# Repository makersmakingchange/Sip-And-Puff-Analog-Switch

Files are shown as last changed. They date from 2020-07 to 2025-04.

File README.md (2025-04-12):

# Sip and Puff Switch

The Sip and Puff Switch is an assistive technology that enables a user to control a device by using their mouth to "sip"(inhale) or "puff"(exhale) on a straw, tube or ‘wand’. It is primarily used by people with limited or no limb movement. The Sip and Puff Switch can be connected directly to an assistive device with a 3.5 mm jack or to a computer or smartphone using a suitable switch interface.

The Sip and Puff Switch has two 3.5 mm mono outputs so it can control two devices. The sip threshold and puff threshold are adjustable. The switch is powered by two CR2032 lithium coin cell batteries.

## More info at

- [Makers Making Change Project Page](https://www.makersmakingchange.com/project/sip-and-puff-switch/)

## Getting Started

### 1. Order the Off-The-Shelf Components
The [Bill of Materials](/Documentation/SPA_BOM_v1.0.xlsx) lists all of the parts and components required to build the Sip and Puff switch.

### 2. Order the Custom Printed Circuit Board (PCB)
The Sip and Puff Switch uses a custom PCB to mount all of the electronic components. Refer to [MMC_PCB_Fabrication_Manual](/Documentation/MMC_PCB_Fabrication_Manual.pdf) for information on how to order a custom PCB. For convenience, the final generated Gerber files for several PCB manufacturers are listed below. If you want to use a different manufacturer, instructions for converting the original [Eagle Files](/Design_Files/PCB/Eagle_Files) are also included in the MMC PCB Fabrication Manual.

| PCB Manufacturer                	| Website                                 	| Gerber Files                                                                                                        	|
|---------------------------------	|-----------------------------------------	|-------------------------------------------------------------------------------------------------------------	|
| JLCPCB                          	| https://jlcpcb.com/                     	|  [JLCPCB_Sip_And_Puff_Analog_Switch.zip](/Build_Files/PCB/JLCPCB_Sip_And_Puff_Analog_Switch.zip)             	|
| OSH Park                        	| https://oshpark.com/                    	| [OSHPark_Sip_And_Puff_Analog_Switch.zip](/Build_Files/PCB/OSHPark_Sip_And_Puff_Analog_Switch.zip)           	|
| Seeed Fusion PCB                	| https://www.seeedstudio.com/fusion.html 	| [Seeed_Fusion_Sip_And_Puff_Analog_Switch.zip](/Build_Files/PCB/Seeed_Fusion_Sip_And_Puff_Analog_Switch.zip) 	|

### 3. Print the 3D Printable components

Print the components for the enclosure and the mouthpiece mount: [3D Printing Files](/Build_Files/3D_Printing/). Total print time for the enclosure components is approximately 4.5 hours and for the mouthpiece mount components is approximately 2.5 hours.  

### 4. Assemble the Switch and Mouthpiece Mount

Reference the assembly instructions for the [Sip and Puff Switch](/Documentation/SPA_Assembly_v1.0.pdf) and the assembly instructions for the [Mouthpiece Stand](/Documentation/SPA_MPStand_Assembly_v1.0.pdf) for the tools and steps required to build each portion.

## Files

### Documentation
| Document                        	| Version 	| Link                                                                         	|
|---------------------------------	|---------	|------------------------------------------------------------------------------	|
| Design Specification            	| WIP     	|                                                                              	|
| Design Rationale                	| WIP     	|                                                                              	|
| Bill of Materials               	| 1.0     	| [SPA_BOM](/Documentation/SPA_BOM_v1.0.xlsx)                                  	|
| Assembly Guide                  	| 1.0     	| [SPA_Assembly](/Documentation/SPA_Assembly_v1.0.pdf)                         	|
| Mouthpiece Mount Assembly Guide 	| 1.0     	| [SPA_MPStand_Assembly](/Documentation/SPA_MPStand_Assembly_v1.0.pdf)         	|
| Maker Checklist                 	| 1.0     	| [SPA_Checklist](/Documentation/SPA_Checklist_v1.0.pdf)                       	|
| Quick Guide                     	| 1.0     	| [SPA_Checklist](/Documentation/SPA_Quick_Guide_v1.0.pdf)                      |
| User Guide                      	| 1.0     	| [SPA_Checklist](/Documentation/SPA_User_Guide_v1.0.pdf)                       |
| Changelog                       	| 1.0     	| [SPA_Changelog](/Documentation/SPA_Changelog_v1.0.pdf)                       	|
| PCB Fabrication Manual          	| 0.1     	| [MMC_PCB_Fabrication_Manual](/Documentation/MMC_PCB_Fabrication_Manual.pdf)  	|

### Design Files
 - [Enclosure CAD Files](/Design_Files/CAD/Enclosure)
 - [Mouthpiece Mount CAD Files](/Design_Files/CAD/Mouthpiece_Mount)
 - [PCB Files](/Design_Files/PCB/Eagle_Files)

### Build Files
 - [3D Printing Files](/Build_Files/3D_Printing)
 - [PCB Files](/Build_Files/PCB/Gerber_Files)

## License
Everything needed or used to design, make, test, or prepare the Analog Sip and Puff Switch is licensed under the CERN 2.0 Persmissive license <https://ohwr.org/project/cernohl/wikis/Documents/CERN-OHL-version-2> (CERN-OHL-P) .

Accompanying material such as instruction manuals, videos, and other copyrightable works that are useful but not necessary to design, make, test, or prepare the Analog Sip and Puff Switch are publshed under a Creative Commons Attribution-ShareAlike 4.0 license <https://creativecommons.org/licenses/by-sa/4.0/> (CC BY-SA 4.0)

<!-- ABOUT MMC START -->
## About Makers Making Change
[Makers Making Change Logo](https://www.makersmakingchange.com/)

Makers Making Change is a program of [Neil Squire](https://www.neilsquire.ca/), a Canadian non-profit that uses technology, knowledge, and passion to empower people with disabilities.

Makers Making Change leverages the capacity of community based Makers, Disability Professionals and Volunteers to develop and deliver affordable Open Source Assistive Technologies.

 - Website: [www.MakersMakingChange.com](https://www.makersmakingchange.com/)
 - GitHub: [makersmakingchange](https://github.com/makersmakingchange)
 - Bluesky: [@makersmakingchange.bsky.social](https://bsky.app/profile/makersmakingchange.bsky.social)
 - Instagram: [@makersmakingchange](https://www.instagram.com/makersmakingchange)
 - Facebook: [makersmakechange](https://www.facebook.com/makersmakechange)
 - LinkedIn: [Neil Squire Society](https://www.linkedin.com/company/neil-squire-society/)
 - Thingiverse: [makersmakingchange](https://www.thingiverse.com/makersmakingchange/about)
 - Printables: [MakersMakingChange](https://www.printables.com/@MakersMakingChange)

### Contact Us
For technical questions, to get involved, or to share your experience we encourage you to [visit our website](https://www.makersmakingchange.com/) or [contact us](https://www.makersmakingchange.com/s/contact).
<!-- ABOUT MMC END -->

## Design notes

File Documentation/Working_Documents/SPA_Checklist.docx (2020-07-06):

To-do

- Acquire off-the-shelf components
- Print 3D printable components
- Assemble the switch
- Test the switch
- Clean and disinfect the switch
- Package the switch in a sealed bag
- Print the Quick Guide

Items to Deliver to User

- Assembled, Tested, and cleaned Sip and Puff Switch
- Quick Guide

© 2020 by Neil Squire. “Sip and Puff Switch Maker Checklist” is licensed under the CC BY SA 4.0 License: http://creativecommons.org/licenses/by-sa/4.0 PAGE 1 OF 3 Design files available at https://www.makersmakingchange.com/project/sip-and-puff-switch/

V1.0 | JUNE 2020 Sip and Puff Switch MAKER CHECKLIST

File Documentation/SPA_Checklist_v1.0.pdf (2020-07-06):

V1.0 | JUNE 2020

# Sip and Puff Switch

MAKER CHECKLIST

© 2020 by Neil Squire. (https://neilsquire.ca/) “Sip and Puff Switch Maker Checklist” is licensed under the CC BY SA 4.0 License: http://creativecommons.org/licenses/by-sa/4.0

Design files available at https://www.makersmakingchange.com/project/sip-and-puff-switch/ | PAGE 1 OF 1

To-do

ð Acquire off-the-shelf components ð Print 3D printable components ð Assemble the switch
ð Test the switch
ð Clean and disinfect the switch
ð Package the switch in a sealed bag ð Print the Quick Guide

Items to Deliver to User

ð Assembled, Tested, and cleaned Sip and Puff Switch
ð Quick Guide

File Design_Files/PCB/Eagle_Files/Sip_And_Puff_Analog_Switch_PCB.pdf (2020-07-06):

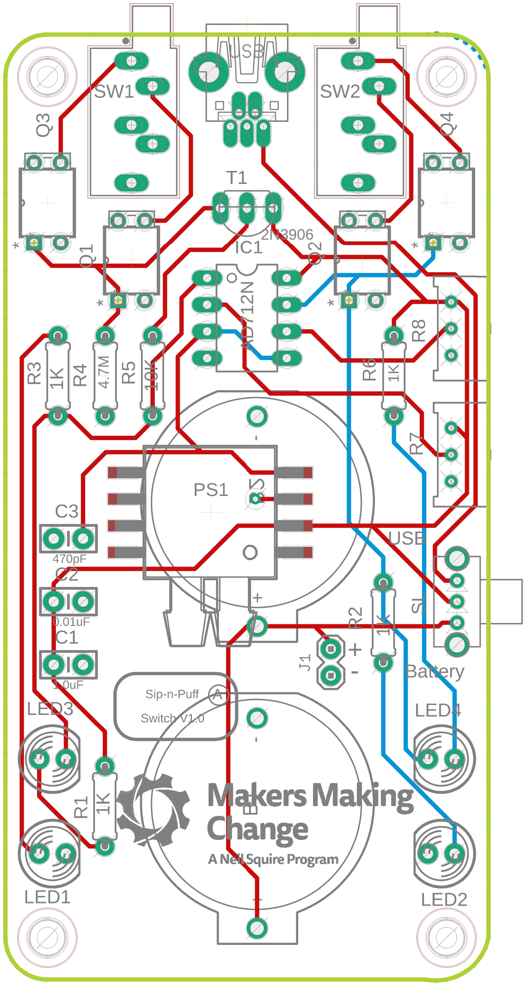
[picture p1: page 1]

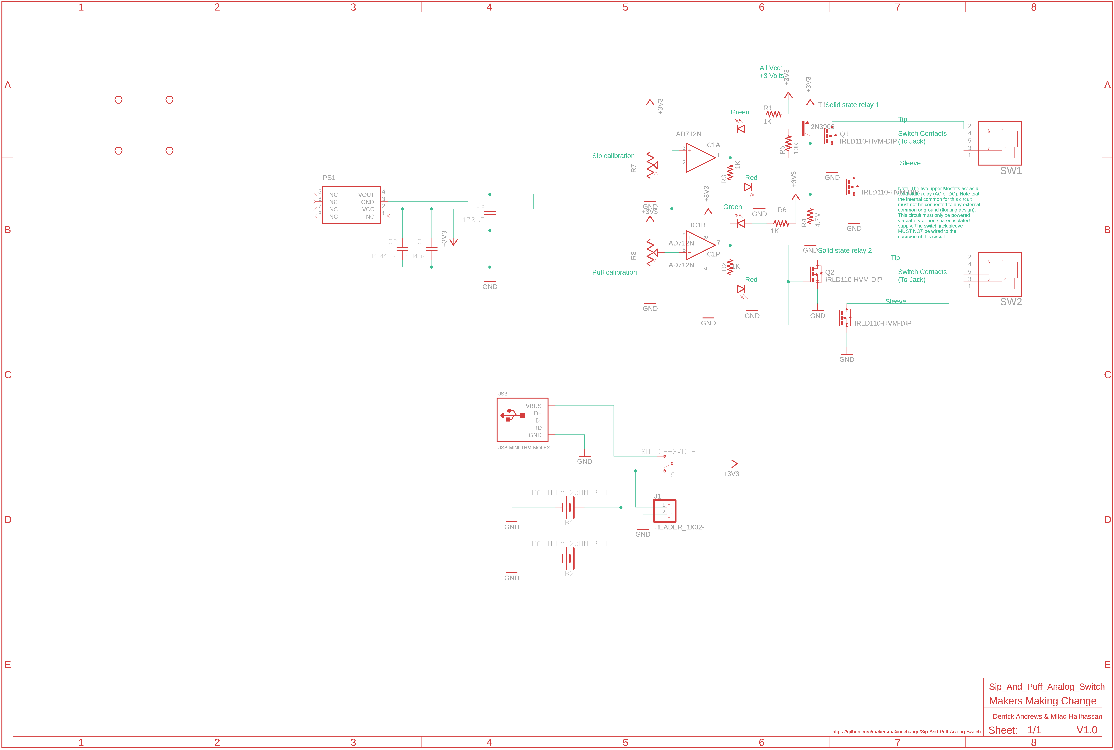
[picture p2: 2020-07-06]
Design_Files/PCB/Eagle_Files/Sip_And_Puff_Analog_Switch_sch.png

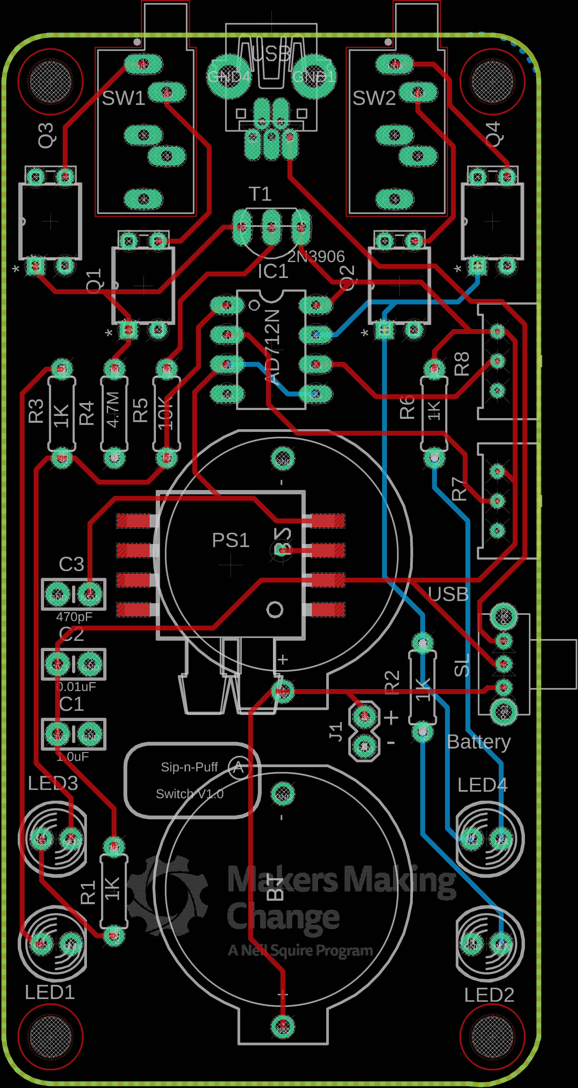
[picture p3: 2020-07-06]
Design_Files/PCB/Eagle_Files/Sip_And_Puff_Analog_Switch_brd.png

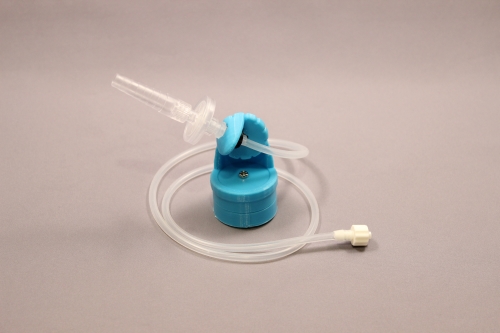
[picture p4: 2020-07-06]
Photos/SPA_Mouthpiece_Mount.JPG

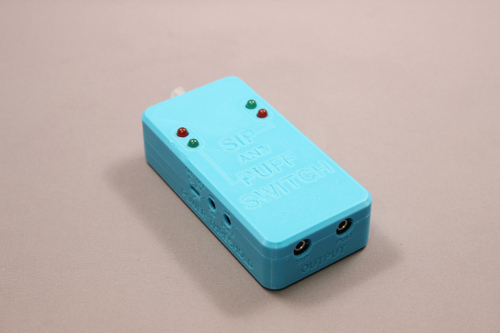
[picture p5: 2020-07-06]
Photos/SPA_Enclosure.JPG

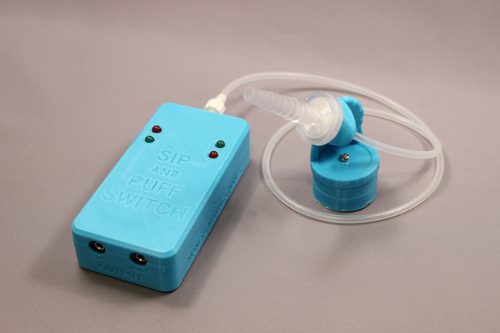
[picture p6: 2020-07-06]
Photos/Sip-And-Puff-Switch.JPG

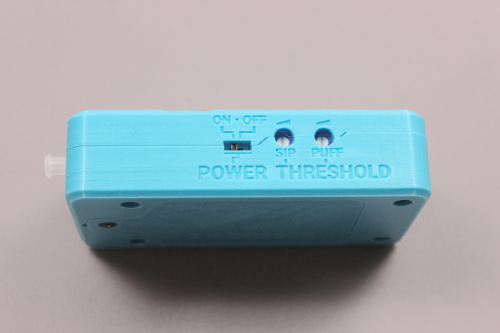
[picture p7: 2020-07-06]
Photos/SPA_Enclosure2.JPG

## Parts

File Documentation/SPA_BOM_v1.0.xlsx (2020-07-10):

ID | SubAssembly | Type | Qty | Component | Component name | Vendor | Manufacturer | MPN | Part Number | Pkg Qty | Pkg Cost (CAD) | Unit Cost | Pkg ReqD | MinCost | Extended Cost (CAD) | Sub-Assembly | Link
 | Switch |  |  |  | Sip and Puff Switch |  |  |  |  |  |  |  |  | $285.00 |  | $111.53
 | PCB Component |  |  |  |  |  |  |  |  |  |  |  |  |  |  | $48.26
 | PCB Component | COTS | 1 | PS1 | IC PRESSURE SENSOR 8-SOP 3V | Digikey Canada | NXP USA Inc. | MP3V5004GP-ND | MP3V5004GP-ND | 1 | $21.94 | 21.94 | 1 | $21.94 | $21.94 |  | https://www.digikey.ca/products/en?keywords=MP3V5004GP-ND
 | PCB Component | COTS | 2 | SW1,SW2 | CONN JACK STEREO 3.5MM R/A | Digikey Canada | CUI Devices | SJ1-3535NG | CP1-3535NG-ND | 1 | $1.70 | 1.7 | 2 | $3.40 | $3.40 |  | https://www.digikey.ca/product-detail/en/cui-devices/SJ1-3535NG/CP1-3535NG-ND/738699
 | PCB Component | COTS | 1 | IC1 | OP AMP 2Ch RR | Digikey Canada | Microchip inc. | MCP6002-I/P | MCP6002-I/P-ND | 1 | $2.16 | 2.16 | 1 | $2.16 | $2.16 |  | https://www.digikey.ca/product-detail/en/microchip-technology/MCP6002-I-P/MCP6002-I-P-ND/500875
 | PCB Component | COTS | 2 | LED2,LED4 | GREEN LED | Digikey Canada | Lite-On Inc. |  | 160-1852-ND | 1 | $0.50 | 0.5 | 2 | $1.00 | $1.00 |  | https://www.digikey.ca/products/en?keywords=LTL2R3KGD-EM
 | PCB Component | COTS | 1 | C3 | CAP CER 470PF 50V X7R RADIAL | Digikey Canada | KEMET | C315C471K5R5TA | 399-9740-ND | 1 | $0.50 | 0.5 | 1 | $0.50 | $0.50 |  | http://www.digikey.ca/product-detail/en/kemet/C315C471K5R5TA/399-9740-ND
 | PCB Component | COTS | 1 | C2 | CAP CER 10000PF 50V X7R RADIAL | Digikey Canada | KEMET | C315C103K5R5TA7303 | 399-9858-1-ND | 1 | $0.37 | 0.37 | 1 | $0.37 | $0.37 |  | https://www.digikey.ca/product-detail/en/kemet/C315C103K5R5TA7303/399-9858-1-ND
 | PCB Component | COTS | 1 | C1 | CAP CER 1UF 25V X7R RADIAL | Digikey Canada | KEMET | C315C105K3R5TA | 399-9714-ND | 1 | $1.13 | 1.13 | 1 | $1.13 | $1.13 |  | https://www.digikey.ca/product-detail/en/kemet/C315C105K3R5TA/399-9714-ND
 | PCB Component | COTS | 2 | LED1,LED3 | RED LED | Digikey Canada | Lite-On Inc. | LTL2R3KRD-EM | 160-1853-ND | 1 | $0.50 | 0.5 | 2 | $1.00 | $1.00 |  | https://www.digikey.ca/en/products/detail/lite-on-inc/LTL2R3KRD-EM/2675133
 | PCB Component | COTS | 1 | SL | SWITCH SLIDE SPDT 100MA 12V | Digikey Canada | C&K | OS102011MA1QN1 | CKN9559-ND | 1 | $0.73 | 0.73 | 1 | $0.73 | $0.73 |  | https://www.digikey.ca/product-detail/en/c-k/OS102011MA1QN1/CKN9559-ND/1981430
 | PCB Component | COTS | 4 | Q1-Q4 | MOSFET N-CH 100V 1A 4-DIP | Digikey Canada | Vishay Siliconix | IRLD110PBF | IRLD110PBF-ND | 1 | $1.32 | 1.32 | 4 | $5.28 | $5.28 |  | https://www.digikey.ca/product-detail/en/vishay-siliconix/IRLD110PBF/IRLD110PBF-ND/812489
 | PCB Component | COTS | 1 | Q5 | TRANSISTOR, PNP 2N3906 | Digikey Canada | ON Semiconductor | 2N3906 | 2N3906D26ZCT-ND | 1 | $0.34 | 0.34 | 1 | $0.34 | $0.34 |  | https://www.digikey.ca/product-detail/en/fairchild-on-semiconductor/2N3906TFR/2N3906D26ZCT-ND
 | PCB Component | COTS | 2 | B1 B2 | Battery holder | Digikey Canada | MPD (Memory Protection Devices) | BS-7 | BS-7-ND | 1 | $1.19 | 1.19 | 2 | $2.38 | $2.38 |  | https://www.digikey.ca/product-detail/en/mpd-memory-protection-devices/BS-7/BS-7-ND/389447
 | PCB Component | COTS | 1 | R4 | 4.7M RESISTOR | Digikey Canada | STACKPOLE | CF14JT4M70 | CF14JT4M70CT-ND | 1 | $0.16 | 0.16 | 1 | $0.16 | $0.16 |  | https://www.digikey.ca/en/products/detail/stackpole-electronics-inc/CF14JT4M70/1741430
 | PCB Component | COTS | 1 | R5 | 10K RESISTOR | Digikey Canada | STACKPOLE | CF14JT10K0CT | CF14JT10K0CT-ND | 1 | $0.16 | 0.16 | 1 | $0.16 | $0.16 |  | https://www.digikey.ca/products/en?keywords=CF14JT10K0CT-ND
 | PCB Component | COTS | 4 | R1,R2,R3,R6 | 1K RESISTOR | Digikey Canada | STACKPOLE | CF14JT1K00 | CF14JT1K00-ND | 1 | $0.16 | 0.16 | 4 | $0.64 | $0.64 |  | https://www.digikey.ca/en/products/detail/stackpole-electronics-inc/CF14JT1K00/1741314
 | PCB Component | COTS | 1 | J1 | CONN HEADER VERT 2POS 2.54MM | Digikey Canada | Sullins Connector Solutions | PREC002SAAN-RC | S1012EC-02-ND | 1 | $0.09 | 0.09 | 1 | $0.09 | $0.09 |  | https://www.digikey.ca/en/products/detail/sullins-connector-solutions/PREC002SAAN-RC/2774852
 | PCB Component | COTS | 2 | R7,R8 | 10K TRIMMER RESISTOR | Digikey Canada | Bourns Inc. | 3386C-103LF | 3386C-103LF-ND | 1 | $3.49 | 3.49 | 2 | $6.98 | $6.98 |  | https://www.digikey.ca/product-detail/en/bourns-inc/3386C-1-103LF/3386C-103LF-ND/1088475
 |  |  |  |  |  |  |  |  |  |  |  |  |  |  | $0.00
 | PCB |  |  |  |  |  |  |  |  |  |  |  |  |  |  | $3.00
 | PCB | Custom PCB | 1 | PCB | PCB | Varies |  |  |  | 5 | $15.00 | 3 | 1 | $15.00 | $3.00 |  | e.g. https://www.pcbway.com/ 25-40 day shipping
 |  |  |  |  |  |  |  |  |  |  |  |  |  |  | $0.00
 | Enclosure |  |  |  |  |  |  |  |  |  |  |  |  |  |  | $54.45
 | Enclosure | 3D Printed | 1 | Case Top | Case, Top | n/a |  |  |  | 1 | $0.55 | 0.55 | 1 | $0.55 | $0.55 |  | https://github.com/makersmakingchange/Sip-And-Puff-Analog-Switch/blob/master/Build_Files/3D_Printing/SPA_Encl_Top.stl
 | Enclosure | 3D Printed | 1 | Case Bottom | Case, Bottom | n/a |  |  |  | 1 | $0.50 | 0.5 | 1 | $0.50 | $0.50 |  | https://github.com/makersmakingchange/Sip-And-Puff-Analog-Switch/blob/master/Build_Files/3D_Printing/SPA_Encl_Bottom.stl
 | Enclosure | 3D Printed | 1 | Battery Cover | Case, Battery Cover | n/a |  |  |  | 1 | $0.19 | 0.19 | 1 | $0.19 | $0.19 |  | https://github.com/makersmakingchange/Sip-And-Puff-Analog-Switch/blob/master/Build_Files/3D_Printing/SPA_Encl_Battery_Cover.stl
 | Enclosure | 3D Printed | 4 | LED Spacers | Case, LED Spacers | n/a |  |  |  | 1 | $0.01 | 0.01 | 4 | $0.04 | $0.04 |  | https://github.com/makersmakingchange/Sip-And-Puff-Analog-Switch/blob/master/Build_Files/3D_Printing/SPA_Encl_LED_Spacer.stl
 | Enclosure | COTS | 5 | Screws | Sheet metal screw, #4-40, 3/8" Length | Digikey Canada |  |  |  | 1 | $0.32 | 0.32 | 5 | $1.60 | $1.60 |  | https://www.digikey.ca/en/products/detail/keystone-electronics/689/316585
 | Enclosure | COTS | 1 | Internal Tubing | Tubing, 4 mm OD, 2 mm ID | Amazon |  |  |  | 1 | $11.42 | 11.42 | 1 | $11.42 | $11.42 |  | https://www.amazon.ca/Uxcell-a15121600ux1003-Silicone-Grade-Water/dp/B01C3GCZTM
 | Enclosure | COTS | 2 | Leur Lock Nut | Nut, panel | Amazon |  |  |  | 25 | $33.73 | 1.3492 | 1 | $33.73 | $2.70 |  | https://www.amazon.ca/Cole-Parmer-Panel-Mount-Black-Nylon/dp/B003NUUH5C
 | Enclosure | COTS | 1 | Female Leur Lock | Female Luer Bulkhead to Hose Barb Adapter | Cole-Palmer |  |  |  | 25 | $36.47 | 1.4588 | 1 | $36.47 | $1.46 |  | https://www.coleparmer.ca/i/cole-parmer-female-luer-bulkhead-1-4-28-unf-thread-to-3-32-hose-barb-pp-25-pk/4550832
 | Switch | COTS | 2 | Cables | Mono Cable, 5 ft length | Amazon Canada |  |  |  | 2 | $20.04 | 10.02 | 1 | $20.04 | $20.04 |  | https://www.amazon.com/Powers-3-5mm-monaural-Audio-Cable/dp/B017V59Z0W
 | Switch | COTS | 2 | Battery | Battery, 3V, Lithium | Amazon Canada |  | CR2032 |  | 1 | $5.00 | 5 | 2 | $10.00 | $10.00 |  | https://www.amazon.ca/Energizer-CR2032-ECR2032-Battery-Lithium/dp/B00F4LLIJM
MP-8 | Mouthpiece | COTS | 1 | Mouthpiece | Sip and Puff Mouthpiece | Qosina |  | 80102 |  | 10 | $32.70 | 3.27015 | 1 | $32.70 | $3.27 |  | https://www.qosina.com/stepped-male-luer-lock-connector-80102
MP-9 | Mouthpiece | COTS | 1 | Filter | Filter PTFE Hydrophobic 17 mm, 0.2 Micron | Qosina |  | 28213 |  | 10 | $26.85 | 2.68515 | 1 | $26.85 | $2.69 |  | http://www.qosina.com/hydrophobic-filter-with-female-luer-lock-inlet-male-luer-lock-outlet-28213
MP-3 | Mouthpiece | COTS | 1 | Tubing | External Tubing, 4 mm OD, 2 mm ID, 60 mm length |  |  |  |  | 1 |  | 0 | 1 | $0.00 | $0.00 |  | https://www.amazon.ca/Uxcell-a15121600ux1003-Silicone-Grade-Water/dp/B01C3GCZTM
 | Mouthpiece Mount |  |  |  |  |  |  |  |  |  |  |  |  |  |  | $5.82
MP-14 | Mouthpiece Mount | 3D Printed | 1 | SPA_MP_Base | Mouthpiece Base | n/a |  |  |  | 1 | $0.15 | 0.15 | 1 | $0.15 | $0.15 |  | https://github.com/makersmakingchange/Sip-And-Puff-Analog-Switch/blob/master/Build_Files/3D_Printing/SPA_MP_Base.stl
MP-13 | Mouthpiece Mount | 3D Printed | 1 | SPA_MP_Cap | Mouthpiece Cap | n/a |  |  |  | 1 | $0.12 | 0.12 | 1 | $0.12 | $0.12 |  | https://github.com/makersmakingchange/Sip-And-Puff-Analog-Switch/blob/master/Build_Files/3D_Printing/SPA_MP_Cap.stl
MP-1 | Mouthpiece Mount | 3D Printed | 1 | SPA_MP_Lower_Swivel | Mouthpiece Lower Swivel | n/a |  |  |  | 1 | $0.20 | 0.2 | 1 | $0.20 | $0.20 |  | https://github.com/makersmakingchange/Sip-And-Puff-Analog-Switch/blob/master/Build_Files/3D_Printing/SPA_MP_Lower_Swivel.stl
MP-11 | Mouthpiece Mount | 3D Printed | 1 | SPA_MP_M3WingNut | Mouthpiece Wing Nut | n/a |  |  |  | 1 | $0.04 | 0.04 | 1 | $0.04 | $0.04 |  | https://github.com/makersmakingchange/Sip-And-Puff-Analog-Switch/blob/master/Build_Files/3D_Printing/SPA_MP_M3WingNut.stl
MP-2 | Mouthpiece Mount | 3D Printed | 1 | SPA_MP_Top_Swivel | Mouthpiece Top Swivel | n/a |  |  |  | 1 | $0.10 | 0.1 | 1 | $0.10 | $0.10 |  | https://github.com/makersmakingchange/Sip-And-Puff-Analog-Switch/blob/master/Build_Files/3D_Printing/SPA_MP_Top_Swivel.stl
MP-5 | Mouthpiece Mount | COTS | 1 | Tee Nut | Tee Nut, 1/4-in-20 UNC, 5/16-in length | Amazon |  |  |  | 100 | $19.49 | 0.1949 | 1 | $19.49 | $0.19 |  | https://www.amazon.ca/Hillman-Group-180297-Pronged-100-Pack/dp/B000H61YF2
MP-6 | Mouthpiece Mount | COTS | 3 | Nut | Hex Nut, M3 | Digikey Canada |  |  |  | 100 | $6.61 | 0.0661 | 1 | $6.61 | $0.20 |  | https://www.digikey.ca/en/products/detail/b-f-fastener-supply/MHNZ-003/274973
MP-7 | Mouthpiece Mount | COTS | 0 | Leur Lock nut | Nut, Panel Mount, 1/4-28 UNF | Cole-Parmer |  |  |  | 25 | $33.73 | 1.3492 | 0 | $0.00 | $0.00 |  | https://www.amazon.ca/Cole-Parmer-Panel-Mount-Black-Nylon/dp/B003NUUH5C
MP-10 | Mouthpiece Mount | COTS | 0 | Female Leur Lock | Female Luer Bulkhead to Hose Barb Adapter | Cole-Parmer | Cole-Parmer | RK-45508-32 |  | 25 | $36.47 | 1.4588 | 0 | $0.00 | $0.00 |  | https://www.coleparmer.ca/i/cole-parmer-female-luer-bulkhead-1-4-28-unf-thread-to-3-32-hose-barb-pp-25-pk/4550832
MP-12 | Mouthpiece Mount |  | 1 | Male Leur Lock | Male luer with Lock Ring x 1/8" Hose Barb | Amazon | Cole-Parmer | AO-45505-04 |  | 25 | $16.80 | 0.672 | 1 | $16.80 | $0.67 |  | https://www.amazon.ca/Cole-Parmer-AO-45505-04-Male-luer-Nylon/dp/B003NV2T34
MP-4 | Mouthpiece Mount | COTS | 6 | Screws | Machine Screw, M3, 16 mm Length | Digikey Canada |  |  |  | 1 | $0.69 | 0.69 | 6 | $4.14 | $4.14 |  | https://www.digikey.ca/en/products/detail/keystone-electronics/29316/1532210

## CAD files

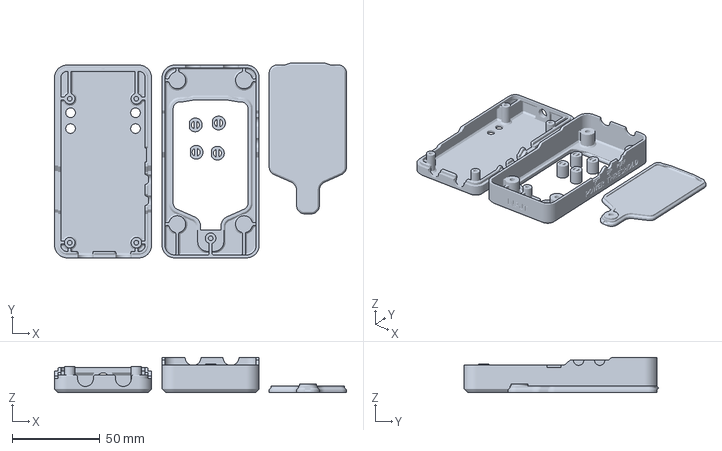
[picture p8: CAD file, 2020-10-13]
Build_Files/3D_Printing/SPA_Encl_Set_PLA.3mf
166.3 x 110.9 x 20.0 mm

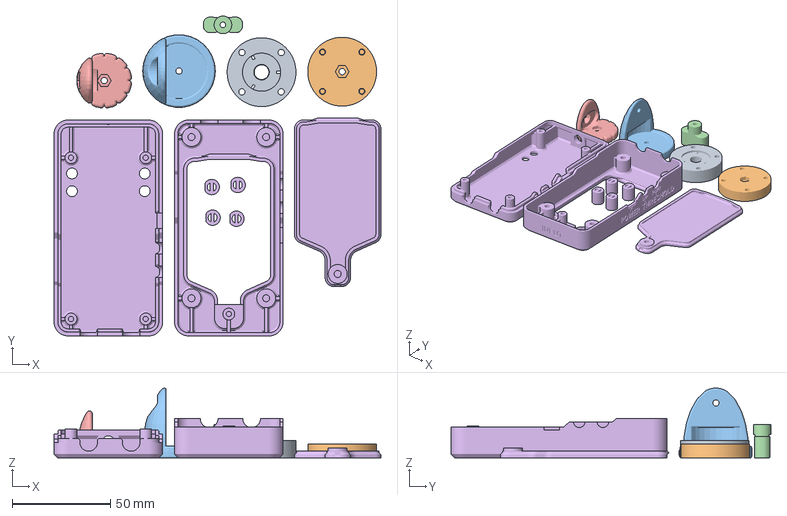
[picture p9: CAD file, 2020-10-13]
Build_Files/3D_Printing/SPA_All-PLA.3mf
166.3 x 162.7 x 35.6 mm
SPA_MP_Base.stl
SPA_MP_Cap.stl
SPA_MP_Lower_Swivel.stl
SPA_MP_M3WingNut.stl
SPA_MP_Top_Swivel.stl
SPA_Encl_Set.stl

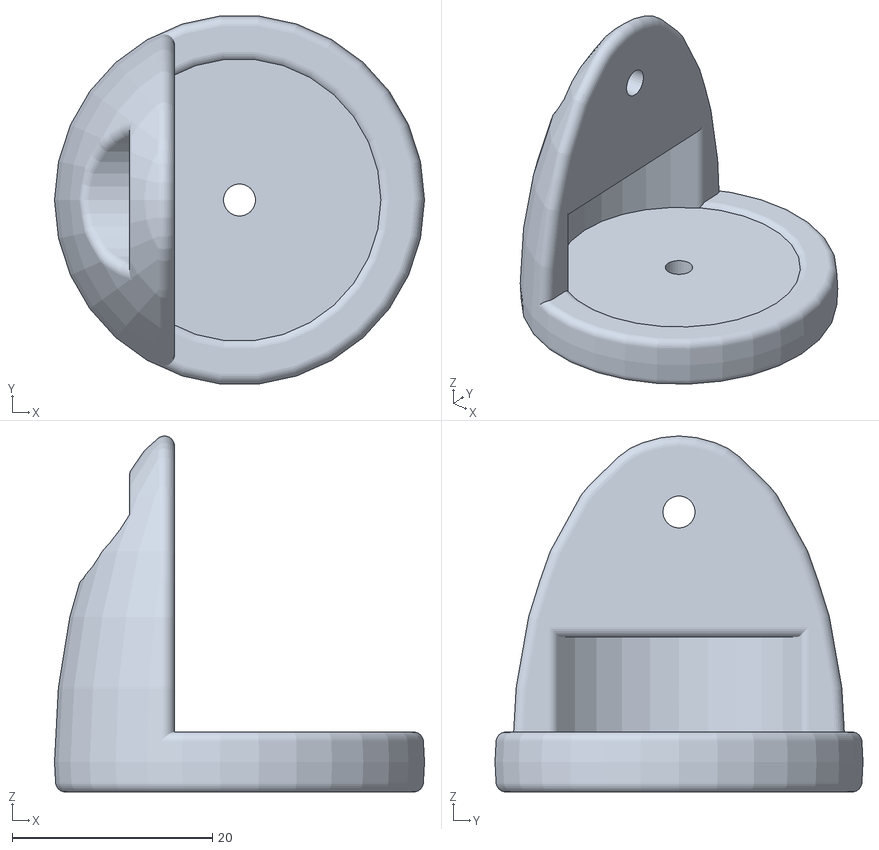
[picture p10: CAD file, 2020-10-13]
Build_Files/3D_Printing/SPA_MP_Lower_Swivel.stl
37.0 x 36.8 x 35.6

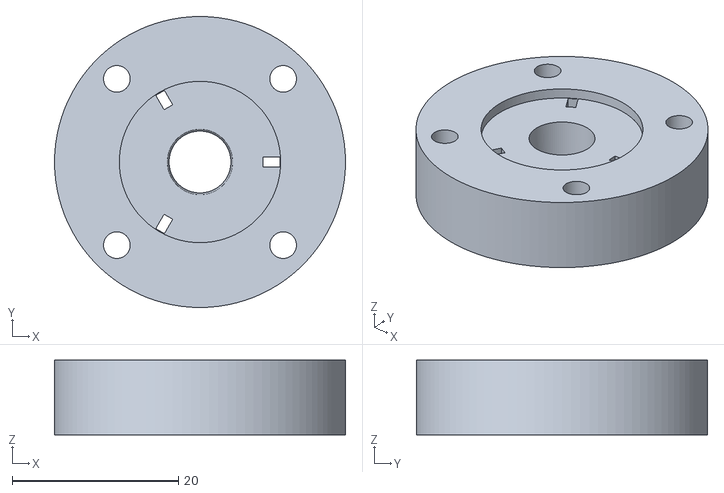
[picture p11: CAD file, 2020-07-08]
Build_Files/3D_Printing/SPA_MP_Base.stl
35.0 x 35.0 x 9.00

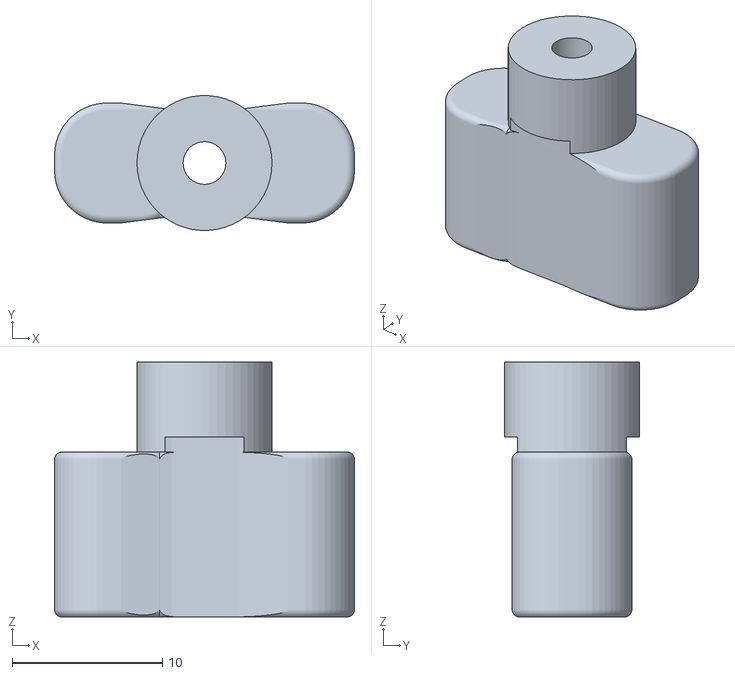
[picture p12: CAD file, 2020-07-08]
Build_Files/3D_Printing/SPA_MP_M3WingNut.stl
20.0 x 8.98 x 17.0

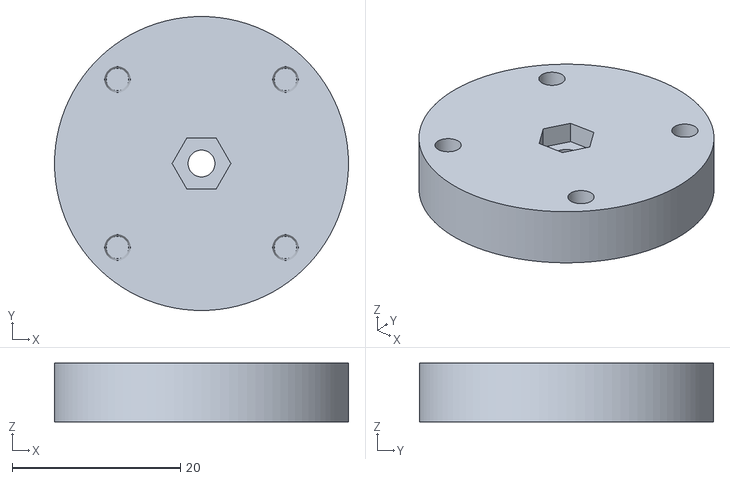
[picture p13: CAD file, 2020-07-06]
Build_Files/3D_Printing/SPA_MP_Cap.stl
35.0 x 35.0 x 7.00

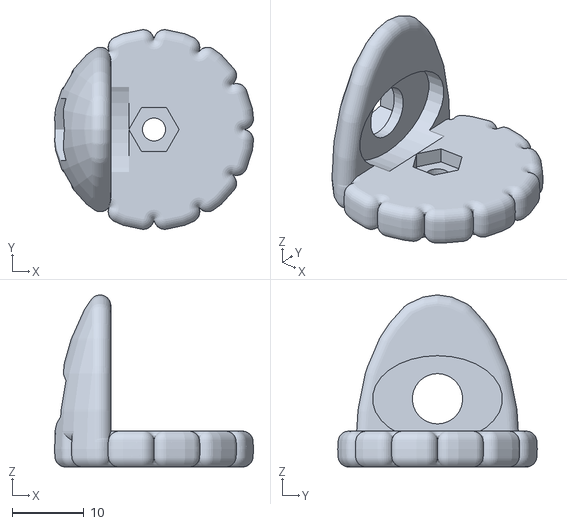
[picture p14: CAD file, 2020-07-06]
Build_Files/3D_Printing/SPA_MP_Top_Swivel.stl
27.7 x 27.8 x 23.9

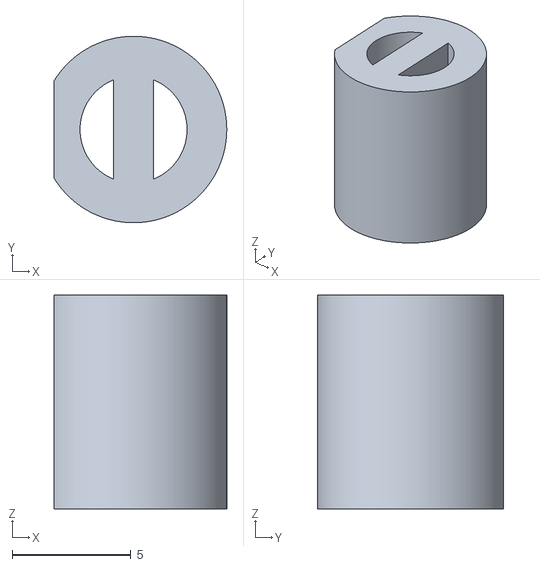
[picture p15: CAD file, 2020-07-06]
Build_Files/3D_Printing/SPA_Encl_LED_Spacer.stl
7.26 x 7.84 x 9.00

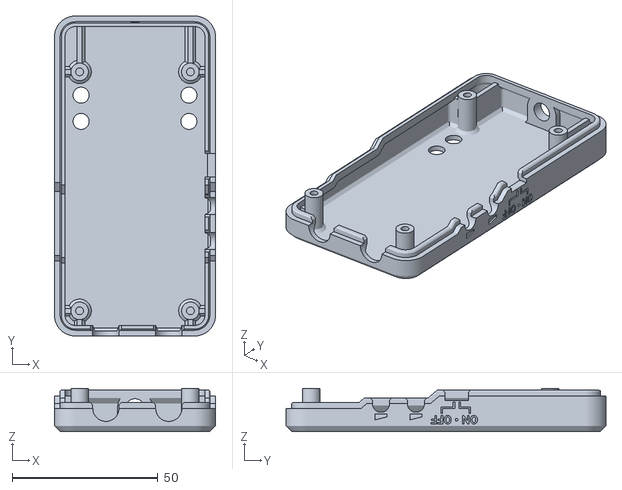
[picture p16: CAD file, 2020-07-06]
Build_Files/3D_Printing/SPA_Encl_Top.stl
55.3 x 109.8 x 14.8

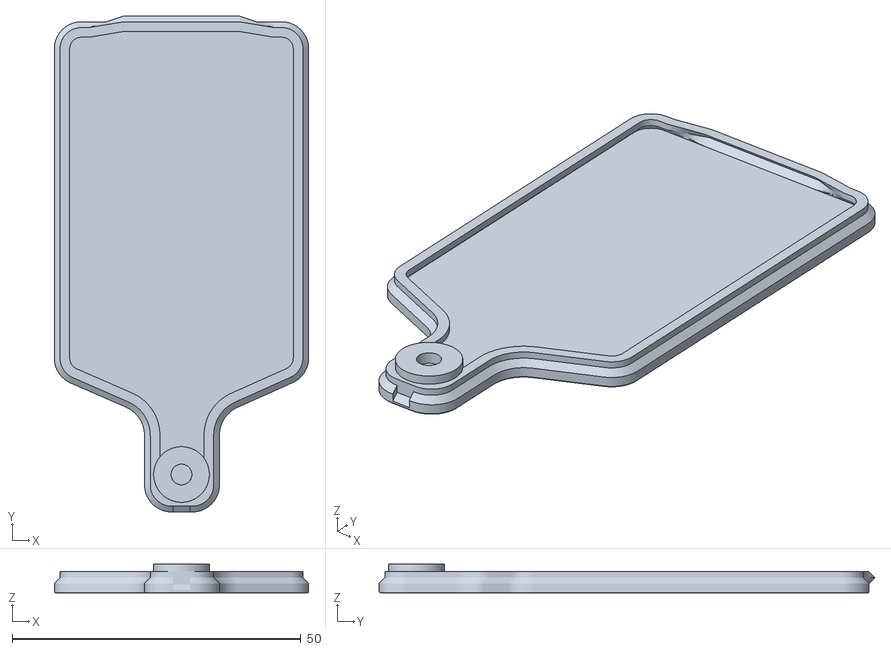
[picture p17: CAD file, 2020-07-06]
Build_Files/3D_Printing/SPA_Encl_Battery_Cover.stl
44.0 x 85.8 x 5.00

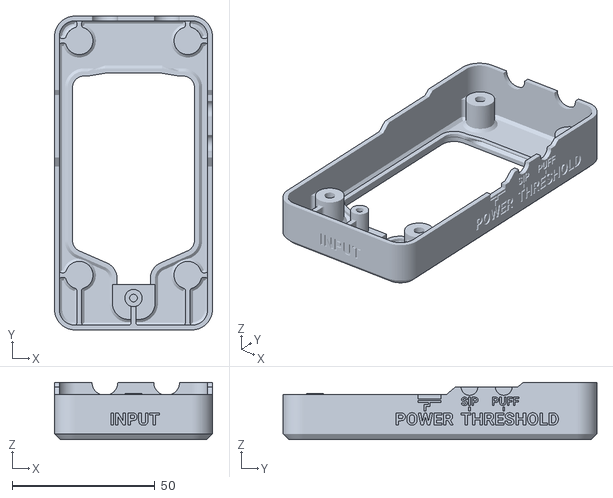
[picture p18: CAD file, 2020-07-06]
Build_Files/3D_Printing/SPA_Encl_Bottom.stl
55.3 x 109.8 x 20.0

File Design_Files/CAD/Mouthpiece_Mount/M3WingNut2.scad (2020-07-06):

$fn=50;
difference(){
union(){
translate([0,0,14])cylinder(d=9,h=6,center=true);
translate([0,0,5.5])
    minkowski(){
    minkowski(){
difference(){

cube([13,1,7], center = true);//Main plate   original cube([90,68,8.5]
 translate([-3,0,0])cube([3,2,7], center = true);//Main plate   original cube([90,68,8.5]      
}

cylinder(d=6,h=3,center=true);
}  //mink
sphere(d=1,center=true,$fn=50);
}  //outer mink
}//end union
translate([0,0,15])cylinder(d1=3,d2=2.8,h=7,center=true);
translate([0,0,12/2])cylinder(d=5.5,h=12,center=true);
ArrayCentItemsVar(0,2,0,77) translate([0,0,12/2])cylinder(d=70,h=12,center=true);
translate([0,0,12])cylinder(d1=4,d2=3,h=1,center=true);
}//end diff






//subs
module ArrayCentItemsVar(xCount,yCount,itemGapX,itemGapY)
{
for (x = [1:xCount]){
for (y = [1:yCount]){
translate([x*itemGapX-(xCount+1)*itemGapX/2,y*itemGapY-(yCount+1)*itemGapY/2,0])
children();
}//for y
}//for x
}//end module
module CircleItems(n,r,myRot)
{
segment=360 / n;
for (i=[1:n])
{
rotate([0, 0, segment*i+myRot])
translate ([r,0,0])
children();
}//for
}//module

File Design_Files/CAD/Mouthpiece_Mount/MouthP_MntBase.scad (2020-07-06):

$fn=100;
//Mouthpiece holder

difference(){
union(){
cylinder(d=35,h=9,center=true);
//translate([-20/2,0,0])cube([20,35,9],center=true);
  
}//end union
cylinder(d1=7.4,d2=8,h=10,center=true);
translate([0,0,9/2])cylinder(d=19.4,h=2.5,center=true); //insert capture
//translate([-8.4,0,20.5])rotate([0,-60,0]) cylinder(d=7,h=100,center=true);//
ArrayCentItems(2,2,20) cylinder(d=3.2,h=10,center=true);// 4 corner holes  
translate([0,0,-5])ArrayCentItems(2,2,20) cylinder(d=5.7,h=4,center=true);// 4 Screw head holes  
CircleItems(3,8.6,0)cube([2,1.2,20], center = true);//(n,r,myRot)
}//end diff
    



//subtractions
//cylinder(d=(D-3/16),h=H);
//translate([0,D/2,H/2])
//translate([-35/2,0,0])cube([35,35,4],center=true);-


// subroutines

module ArrayCentItems(xCount,yCount,itemGap)
{
for (x = [1:xCount]){
for (y = [1:yCount]){
translate([x*itemGap-(xCount+1)*itemGap/2,y*itemGap-(yCount+1)*itemGap/2,0])
children();
}//for y
}//for x
}//end module

module CircleItems(n,r,myRot)
{
segment=360 / n;
for (i=[1:n])
{
rotate([0, 0, segment*i+myRot])
translate ([r,0,0])
children();
}//for
}//module

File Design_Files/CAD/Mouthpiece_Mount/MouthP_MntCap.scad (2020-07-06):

$fn=100;
//Mouthpiece Mount Cap

difference(){
union(){
cylinder(d=35,h=7,center=true);
//translate([-20/2,0,0])cube([20,35,9],center=true);
  
}//end union
cylinder(d=3.2,h=10,center=true);//
translate([0,0,-3])cylinder(d=7,h=4,center=true,$fn=6);//
//translate([0,0,9/2])cylinder(d=19.4,h=2.5,center=true); //insert capture
//translate([-8.4,0,20.5])rotate([0,-60,0]) cylinder(d=7,h=100,center=true);//
translate([0,0,-1])ArrayCentItems(2,2,20) cylinder(d1=3.2,d2=2.6,h=7,center=true);// 4 corner holes  
//translate([0,0,-5])ArrayCentItems(2,2,20) cylinder(d=5.7,h=4,center=true);// 4 Screw head holes  
//CircleItems(3,8.6,0)cube([2,1.2,20], center = true);//(n,r,myRot)
}//end diff
    



//subtractions
//cylinder(d=(D-3/16),h=H);
//translate([0,D/2,H/2])
//translate([-35/2,0,0])cube([35,35,4],center=true);-


// subroutines

module ArrayCentItems(xCount,yCount,itemGap)
{
for (x = [1:xCount]){
for (y = [1:yCount]){
translate([x*itemGap-(xCount+1)*itemGap/2,y*itemGap-(yCount+1)*itemGap/2,0])
children();
}//for y
}//for x
}//end module

module CircleItems(n,r,myRot)
{
segment=360 / n;
for (i=[1:n])
{
rotate([0, 0, segment*i+myRot])
translate ([r,0,0])
children();
}//for
}//module

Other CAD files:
Build_Files/3D_Printing/SPA_All-PETG.3mf
Build_Files/3D_Printing/SPA_Encl_Set.stl
Design_Files/CAD/Mouthpiece_Mount/MouthP_MntLswivel.scad
Design_Files/CAD/Mouthpiece_Mount/MouthP_MntTPswivel.scad

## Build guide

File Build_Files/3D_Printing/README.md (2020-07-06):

# 3D Print Files
All of these components are designed to be printed using a fused filament fabrication (FFF) 3D printer with a 0.4 mm nozzle. Filament color is not critical for function, so it should be left to the end-user's preference or muted tones like black or grey. For material, PLA should be sufficient. If

## Enclosure
| File                       	| Resolution 	| Infill 	| Support 	| Perimeters 	| Qty 	|
|----------------------------	|------------	|--------	|---------	|------------	|-----	|
| SPA_Encl_Battery_Cover.stl 	| 0.2 mm     	| 20%    	| No      	| 2          	| 1   	|
| SPA_Encl_Bottom.stl        	| 0.2 mm     	| 20%    	| No      	| 2          	| 1   	|
| SPA_Encl_LED_Spacer.stl    	| 0.2 mm     	| 20%    	| No      	| 2          	| 4   	|
| SPA_Encl_Top.stl           	| 0.2 mm     	| 20%    	| No      	| 2          	| 1   	|

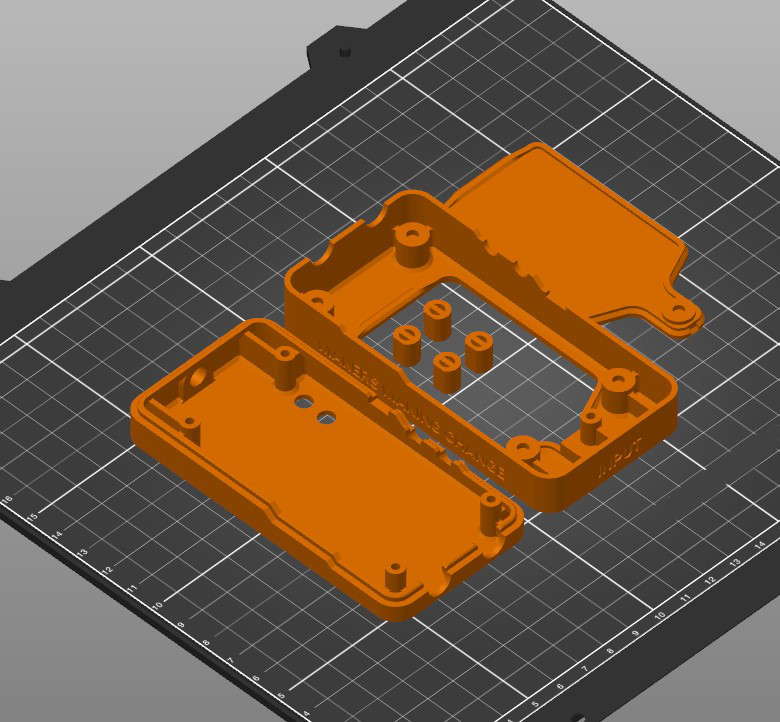
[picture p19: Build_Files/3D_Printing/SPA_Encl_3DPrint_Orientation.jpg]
Screenshot of print orientation


## Mouthpiece Mount
| File                       	| Resolution 	| Infill 	| Support 	| Perimeters 	| Qty 	|
|----------------------------	|------------	|--------	|---------	|------------	|-----	|
| SPA_MP_Base.stl            	| 0.2 mm     	| 20%    	| Yes      	| 2          	| 1   	|
| SPA_MP_Cap.stl             	| 0.2 mm     	| 20%    	| No      	| 2          	| 1   	|
| SPA_MP_Lower_Swivel.stl    	| 0.2 mm     	| 20%    	| Yes      	| 2          	| 1   	|
| SPA_MP_M3WingNut.stl       	| 0.2 mm     	| 20%    	| No      	| 2          	| 1   	|
| SPA_MP_Top_Swivel.stl      	| 0.2 mm     	| 20%    	| Yes      	| 2          	| 1   	|

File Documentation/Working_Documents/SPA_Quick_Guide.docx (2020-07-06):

Analog Sip and Puff: One Page Quick Setup Guide

Notes:

For overview, detailed instructions, cleaning, battery and specs, refer to document: Analog Sip and Puff User Guide

1) Hook up the air tube:

Connect the mouthpiece to the Sip and Puff Switch main box, as shown in Fig1: Fig. 1

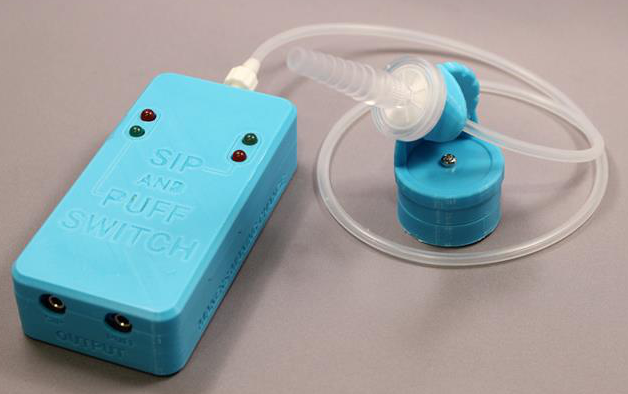
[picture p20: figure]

2) Turn on the main box:

Slide the power switch left, (center of fig 2) towards the air tube connection, using a pen tip.

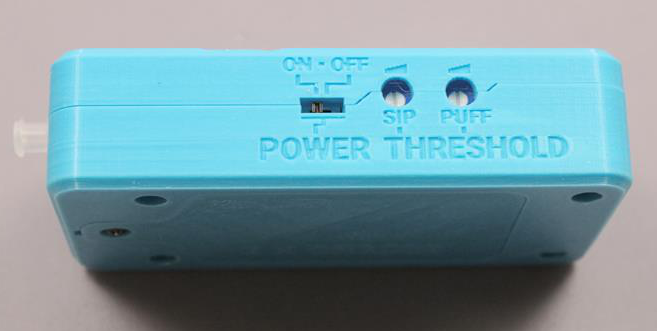
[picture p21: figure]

Fig. 2

3) Reset The Sip and Puff thresholds:

Using a small flat screwdriver, turn both thresholds (Fig2, right of switch) fully clockwise.

4) Set The Sip threshold:

Dial the first adjustment left, until the red (sip) LED just goes out (and stays out).

5) Set The Puff threshold:

Dial Second adjustment left, until the red (puff) LED just goes out (and stays out).

6) Test the unit:

(Disinfect mouthpiece!) Sip and puff on the mouthpiece to confirm proper operation.

The red Puff LED (Left Fig.1) should turn on when you puff on the mouthpiece.

The red Sip LED (Right Fig.1) should turn on when you sip on the mouthpiece.

7) Attach your controlled devices to Sip & Puff switch:

Hook your puff device to 3mm Jack (Fig1, case bottom left) on the main unit.

Hook your sip device to 3mm Jack (Fig1, case bottom right) on the main unit.

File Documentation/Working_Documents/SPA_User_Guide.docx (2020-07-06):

Analog Sip and Puff User GuideFig. 1


Overview:

The MMC Analog Sip and Puff Switch is an assistive switch able to be operated by softly sipping or puffing air in or out of a mouthpiece. The user should have the ability to blow air into, or draw or draw air from a straw . The switch is not recommended for persons who are unable to consciously control air movement in their lungs or mouth. The Analog Sip and Puff Switch consists of a rectangular control box to which an air tube and mouthpiece can be attached. Inside the box there is an air pressure sensor, and two independent momentary switches. The first switch normally triggers when drawing in (sipping) air through the mouthpiece. The second switch normally triggers when blowing (puffing) air through the mouthpiece. The sensitivity level of the sip and puff functions are individually adjustable using two side mounted controls that can be set with a small screwdriver. The internal switches on the unit connect to the external being controlled via two 3mm audio jacks using standard 3mm mono audio cables.

Setup & Adjustment:


Fig. 2

To get started, connect the mouthpiece to the Sip and Puff Switch main box as shown in Fig 1. The unit should be turned on by sliding the power switch (Fig. 2) left, towards the air tube connection, using a pen tip. The switch is recessed to reduce the chance of the unit being turned on or off accidentally. Once the unit is turned on, you should notice some LED’s glowing on the top panel. Normally, you should not see a red LED turned on, unless the user is sipping or puffing into the mouthpiece, as red indicates a triggered (on) state. The quickest way to adjust thresholds, is to use a small screwdriver and dial both adjustments fully clockwise (maximum sensitivity). Then, dial the left (sip) adjustment counterclockwise, until the red sip LED goes out, and the green sip LED (closest to air tube inlet) just stays on. Next, dial the right (sip) adjustment counterclockwise, until the red puff LED goes out, and the green puff LED (furthest from air tube inlet) just stays on. If the sip or puff sensitivity triggers too easily, it’s sensitivity can be reduced by further turning the adjustment counterclockwise.

Installing or changing batteries:

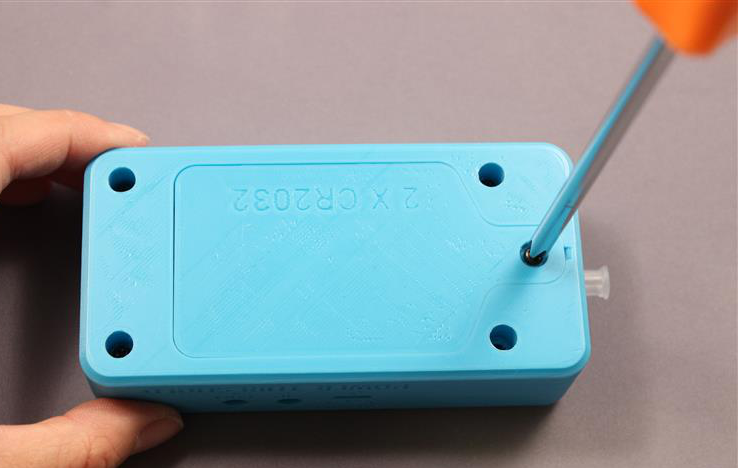
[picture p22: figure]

Fig. 3

The batteries in the Sip and Puff Switch can be changed by using a medium sized Phillips screwdriver, to remove the battery lid screw (closest screw to air tube connector) as shown above.

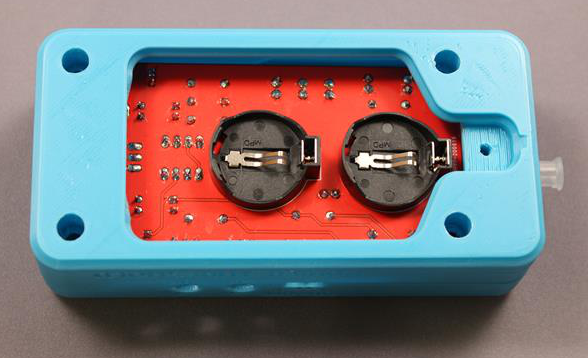
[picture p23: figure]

Fig. 4

The Sip and puff switch accepts two CR2032 coin cells into the round battery holders shown in Fig.4. The battery positive terminal is marked with a ‘+’ which must face up while being installed

Important: The lithium batteries should be changed in pairs to prevent damage to the batteries.

Specifications:

Size: 119mm X 56mm X (the unit sits 11mm higher with the mounting adaptor attached.)

Switch connectors: Dual 3mm mono audio type jacks. Accepts standard 3mm mono plug cables.

Recommended tubing 4mm OD 2mm ID Food

Maximum switching voltage: 48V, DC or AC.

Maximum switching current: 1 Amp, DC or AC.

Battery: Two CR2032 3V cell (replaceable)

Current draw 6.5ma

Expected battery life: 24 hours.

Cleaning: Clean or disinfect with bleach 2 teaspoons of 5 percent laundry bleach in one cup of water.

Do not use alcohol on the air tube or air tube fitting.

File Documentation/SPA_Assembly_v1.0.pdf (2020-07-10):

# Sip & Puff Analog Switch

# ASSEMBLY MANUAL

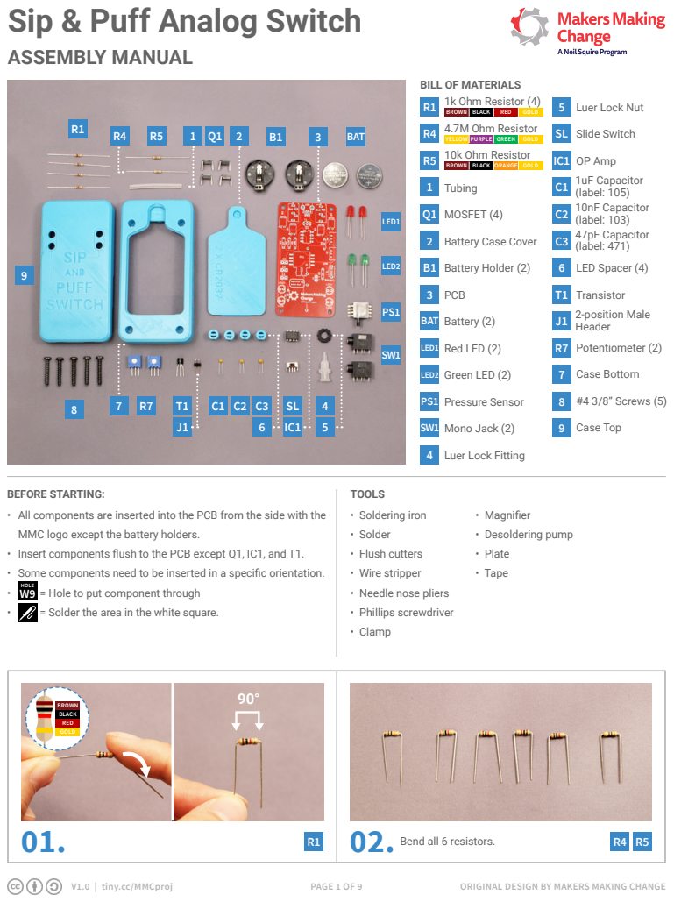
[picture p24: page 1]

BEFORE STARTING:
• All components are inserted into the PCB from the side with the
MMC logo except the battery holders.
• Insert components flush to the PCB except Q1, IC1, and T1.
• Some components need to be inserted in a specific orientation.
• = Hole to put component through
• = Solder the area in the white square.

# Sip & Puff Analog Switch

# ASSEMBLY MANUAL

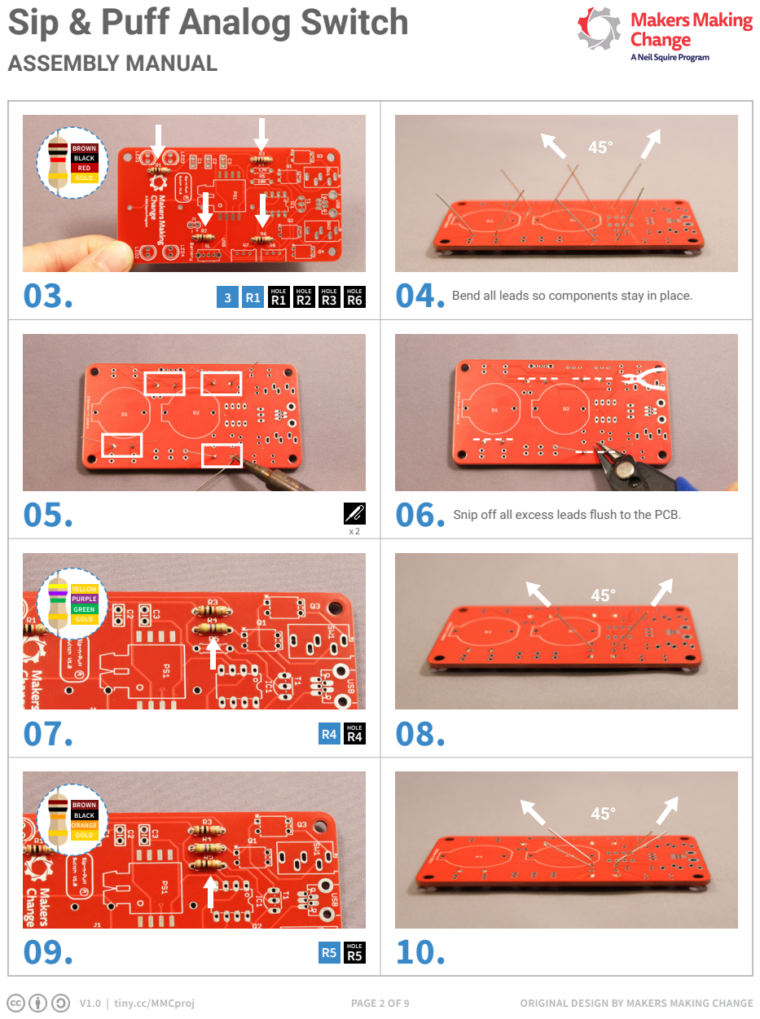
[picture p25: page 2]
V1.0 | tiny.cc/MMCproj; PAGE 2 OF 9; ORIGINAL DESIGN BY MAKERS MAKING CHANGE; BROWN BLACK RED GOLD; YELLOW PURPLE GREEN GOLD; HOLE; BROWN BLACK ORANGE GOLD

R1 | HOLE | HOLE R2 | HOLE R3 | HOLE 3 R6

Bend all leads so components stay in place. R1

Snip off all excess leads flush to the PCB.

# Sip & Puff Analog Switch

# ASSEMBLY MANUAL

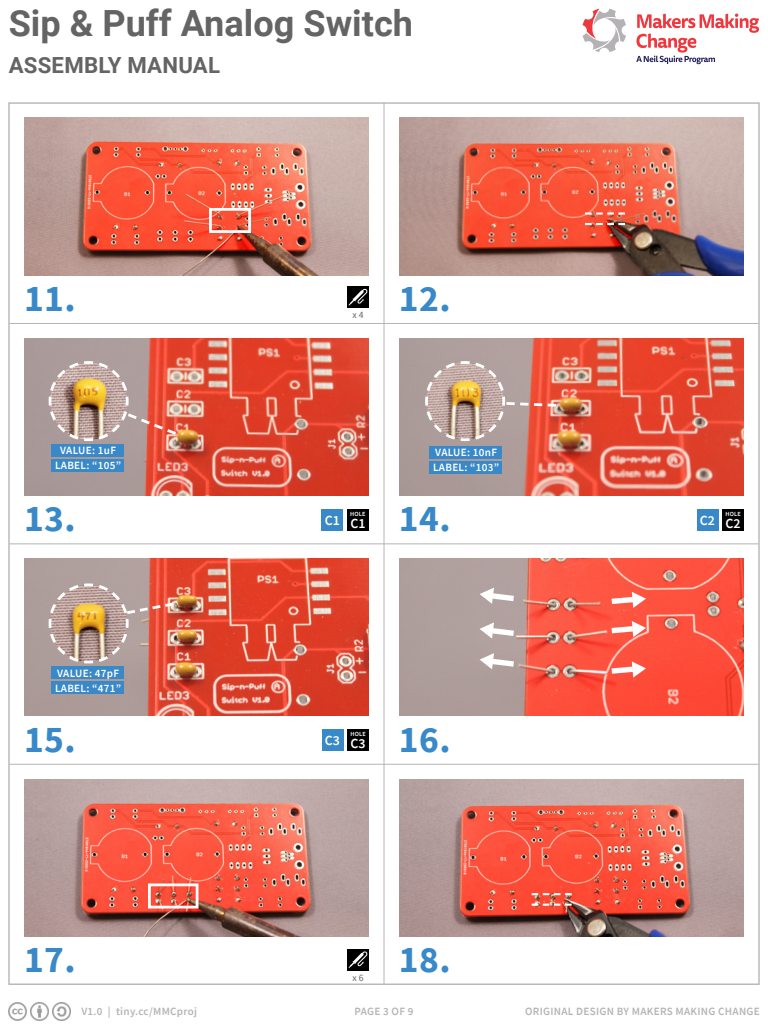
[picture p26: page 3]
V1.0 | tiny.cc/MMCproj; PAGE 3 OF 9; ORIGINAL DESIGN BY MAKERS MAKING CHANGE; VALUE: 1uF LABEL: “105”; VALUE: 47pF LABEL: “471”; HOLE C3; HOLE; C2 HOLE C1; VALUE: 10nF LABEL: “103”

# Sip & Puff Analog Switch

# ASSEMBLY MANUAL

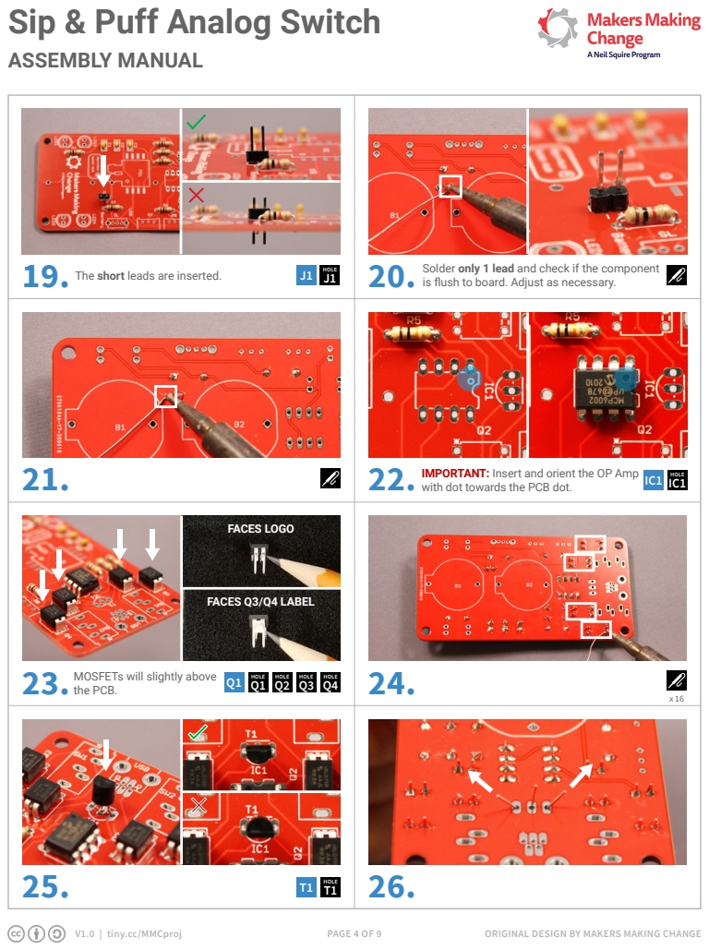
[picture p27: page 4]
V1.0 | tiny.cc/MMCproj; PAGE 4 OF 9; ORIGINAL DESIGN BY MAKERS MAKING CHANGE; 20. The short leads are inserted.; HOLE J1; Solder only 1 lead and check if the component; with dot towards the PCB dot.; HOLE IC1; FACES LOGO; FACES Q3/Q4 LABEL; HOLE; HOLE Q1; HOLE T1

is flush to board. Adjust as necessary.

IMPORTANT: Insert and orient the OP Amp

MOSFETs will slightly above
the PCB.

# Sip & Puff Analog Switch

# ASSEMBLY MANUAL

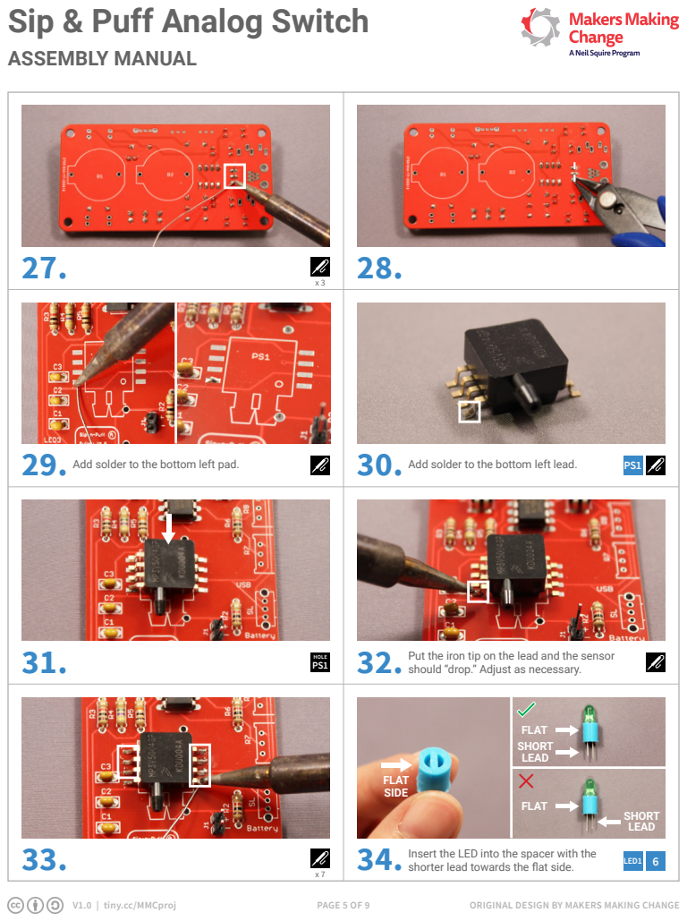
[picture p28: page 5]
V1.0 | tiny.cc/MMCproj; PAGE 5 OF 9; ORIGINAL DESIGN BY MAKERS MAKING CHANGE; Add solder to the bottom left pad.; Add solder to the bottom left lead.; FLAT SIDE; FLAT; SHORT LEAD; LED1; HOLE

Put the iron tip on the lead and the sensor
should “drop.” Adjust as necessary.

Insert the LED into the spacer with the
shorter lead towards the flat side.

# Sip & Puff Analog Switch

# ASSEMBLY MANUAL

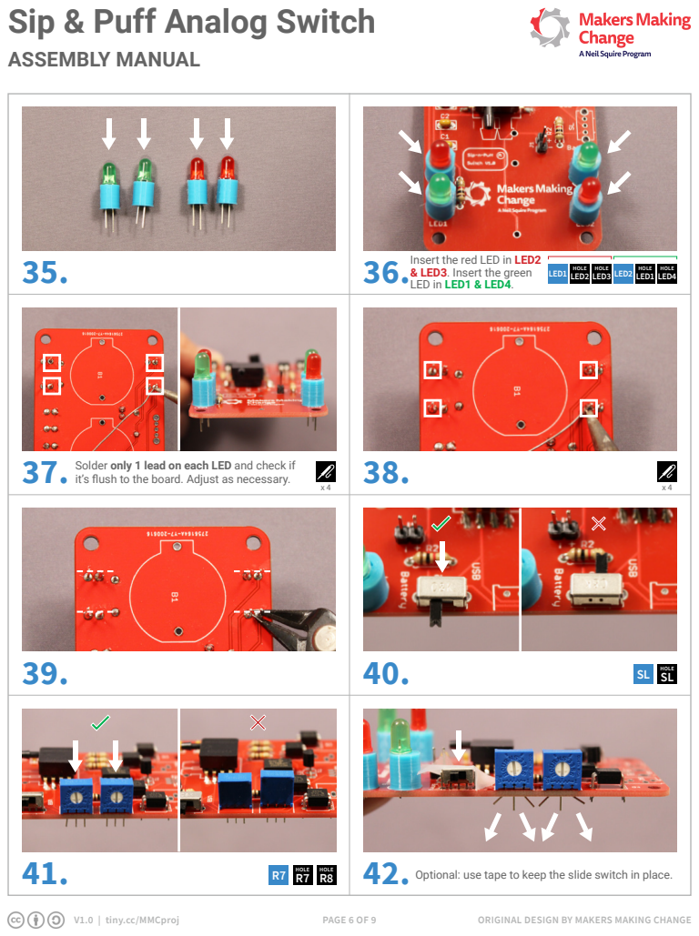
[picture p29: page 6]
V1.0 | tiny.cc/MMCproj; PAGE 6 OF 9; ORIGINAL DESIGN BY MAKERS MAKING CHANGE; LED1; LED3; HOLE; LED4; LED2; HOLE R7; HOLE SL

Insert the red LED in LED2
& LED3. Insert the green
LED in LED1 & LED4.

Solder only 1 lead on each LED and check if
it’s flush to the board. Adjust as necessary.

Optional: use tape to keep the slide switch in place.

# Sip & Puff Analog Switch

# ASSEMBLY MANUAL

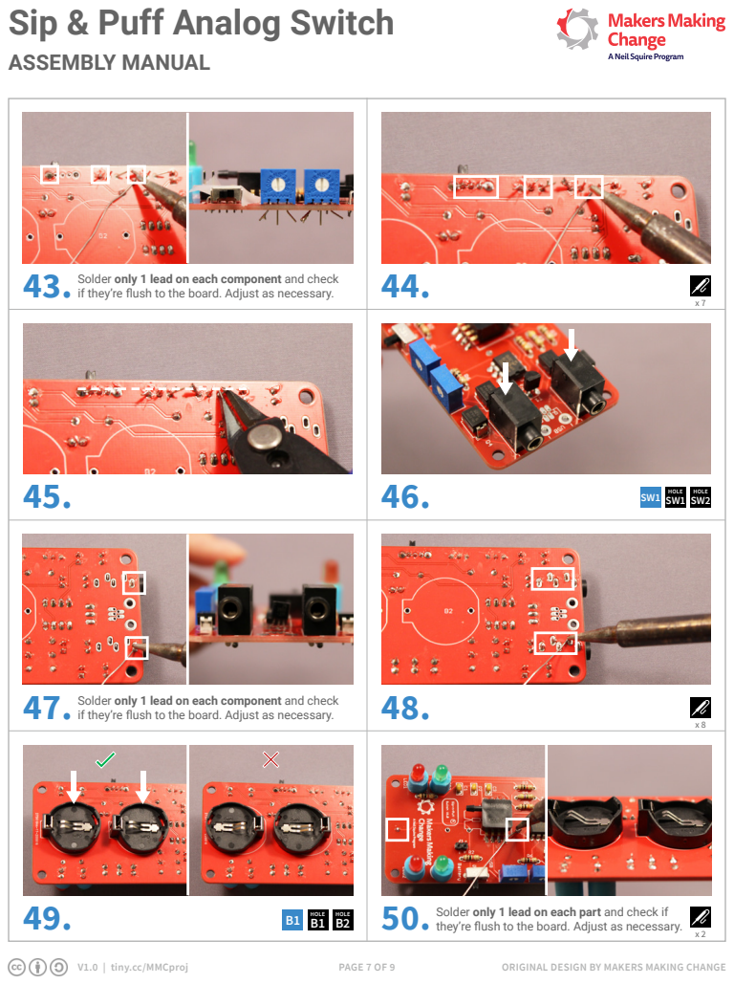
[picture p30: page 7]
V1.0 | tiny.cc/MMCproj; PAGE 7 OF 9; ORIGINAL DESIGN BY MAKERS MAKING CHANGE; if they’re flush to the board. Adjust as necessary.; HOLE; HOLE B1

Solder only 1 lead on each component and check

if they’re flush to the board. Adjust as necessary.

Solder only 1 lead on each part and check if
they’re flush to the board. Adjust as necessary.

# Sip & Puff Analog Switch

# ASSEMBLY MANUAL

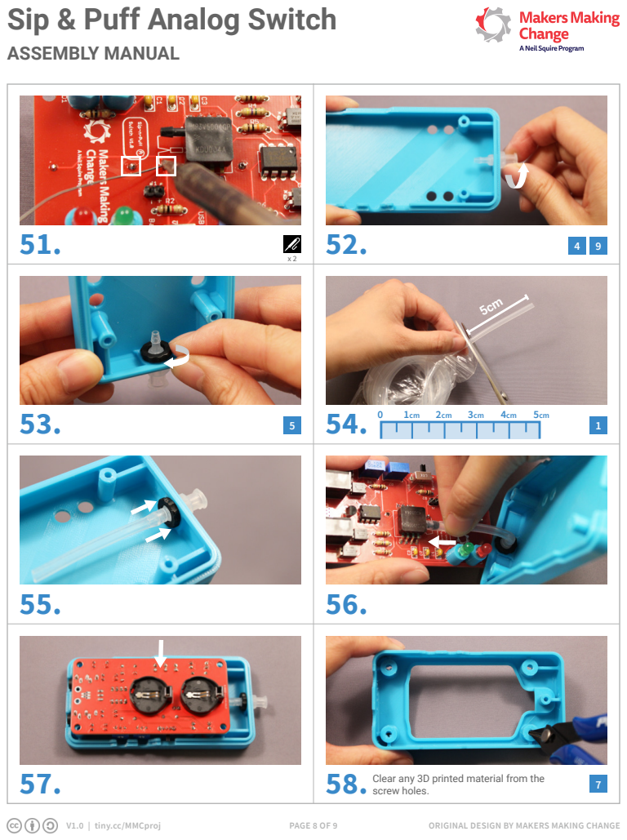
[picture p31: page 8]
V1.0 | tiny.cc/MMCproj; PAGE 8 OF 9; ORIGINAL DESIGN BY MAKERS MAKING CHANGE

Clear any 3D printed material from the
screw holes.

# Sip & Puff Analog Switch

# ASSEMBLY MANUAL

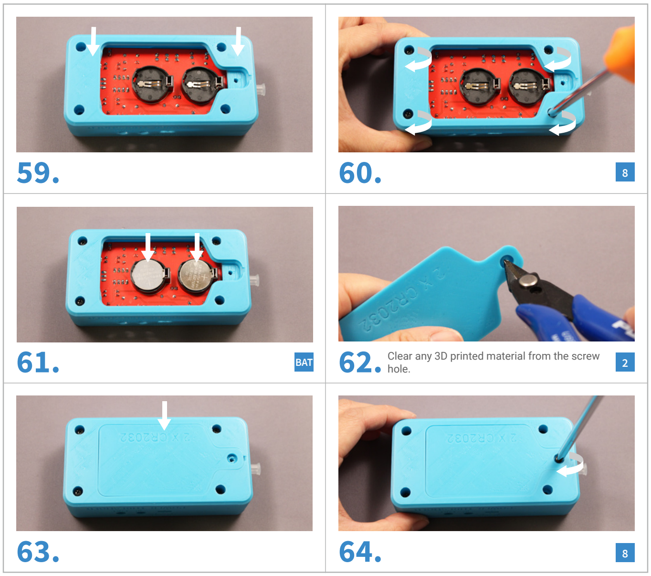
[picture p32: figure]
hole.; BAT

V1.0 | tiny.cc/MMCproj | PAGE 9 OF 9 | ORIGINAL DESIGN BY MAKERS MAKING CHANGE

Clear any 3D printed material from the screw

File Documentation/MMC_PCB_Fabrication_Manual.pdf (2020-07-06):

# MMC PCB Fabrication Manual

Version 0.1
2020/05/05
Author: Milad Hajihassan

Makers Making Change
PCB Fabrication Manual | PCB Fabrication Manual
Version 1.0 | Page 2 of 10

## Table of Contents

## 1. Introduction

## 1.1. What is PCB?

PCB (Printed circuit board) is a board that has lines and pads that connect various points together. The board includes traces that electrically connect the various connectors and components to each other. A PCB allows signals and power to be routed between physical devices. Solder is the metal that makes the electrical connections between the surface of the PCB and the electronic components. [1]

## 1.2. What is PCB Fabrication?

PCB fabrication is the assembly method for circuit boards used in electronic devices. The layers of the board are put together along with the specific surface pattern based on the design files that is used in electronics manufacturing.[2]

## 1.3. What is gerber file?

Users create their own files for manufacturing based on the design files and send them to the manufacturer. The design files for manufacturing PCB is converted to a standard format known as a Gerber file. This is an industry standard for recording the specification of a PCB.[2]

## 2. PCB design tools

There are many different tools for designing PCB’s and you can select any of the available tools based on your previous experience or the requirements of your design. The process of designing PCB is not in the scope of this document but you can find courses or books that can help you understand the process of designing electronics circuits and PCB’s.

Here are the most common PCB design tools:

- Altium Designer (https://www.altium.com/) : Paid with Free Trial and student license.
- Eagle (https://www.autodesk.ca/en/products/eagle/) : Free limited version includes 2 schematic sheets, 2 signal layers, and an 80cm2 (12.4in2) board area.
- Kicad (https://www.kicad-pcb.org/) : Opensource with GNU’s GPL copyright agreement.
- Fritzing (https://fritzing.org/) : Opensource version available on github and the paid application is available. Limited options suitable for basic designs.
- Upverter (https://upverter.com/) : Free cloud-based design tool. It requires sign up for usage.

There are other available tools that can be used to design PCBs.

## 3. How to generate PCB gerber files for fabrication?

Once the PCB board file is created using your favorite PCB design tool then you can generate gerber files which is used by PCB fabrication companies to fabricate your design. The CAM processing tool uses the gerber generator file to create gerber files. The gerber generator file is usually provided by PCB fabrication company of your choice or can be created based on gerber files format which can be found on the website of the PCB fabrication company.

Each PCB board file includes different top and bottom layers and gerber files provide specifications for each of these layers by combining layers together based on the format specified by gerber file generator.

Common layers:

- Top & Bottom Copper
- Top & Bottom Silkscreen
- Top & Bottom Soldermask
- Drill
- Drill Station Info
- Photoplotter Info
- Mill Layer
- Top Paste

There is no standard format for the gerber file generator and there are variations of formats used by PCB fabrication companies.

You can find the final generated gerber files of the projects involving PCB designs for common PCB fabrication companies on our website. You can use the generated gerber files available if you are using one of the fabrication companies listed below or you can create your own gerber files based on PCB design files.

- Seeed Fusion PCB (https://www.seeedstudio.com/fusion.html)
- PCBWay (https://www.pcbway.com/)
- OSH Park ~ (https://oshpark.com/)
- JLCPCB (https://jlcpcb.com/)

We now go over process of generating gerber files using three common PCB design tools.

## Eagle

1. Open the board file of your PCB design using Eagle
2. Select File > CAM Processor
3. Click on “Load job file” dropdown menu button and select “Open CAM file”
4. Download or create the gerber generator file (.cam) used by your PCB fabrication company of your choice
5. Navigate in your system and find the directory that includes the gerber file generator file with. cam extension
6. Select the gerber file generator file and click on “Open” button
7. Double check the Output file layers on left menu bar to make sure there are no layers are missing
8. Click on “Process Job” button
9. Select the output directory (Create a new directory called “gerbers” as an example)
10. The process of creating the gerber file will start and finish once you receive a popup message indicating that “Job Proceed Successfully!”
11. Click on “OK” button
12. Navigate to the directory that includes the generated gerber files (“gerbers” directory as an example)
13. Select all the gerber/drill files in the directory that saved them and generate a compressed file in Zip format.
14. You can now submit the compressed Zip file that includes the gerber files to the PCB fabrication company of your choice.

## Altium designer

1. Open the board file of your .PCB design file using Altium designer. [3]
2. Select File > Fabrication Outputs > Gerber Files
3. Select General setting in Gerber Setup window
4. Set the units in “inches” precision to “2:5” in General setting
5. Select Layers setting in Gerber Setup window
6. Next, make sure you have the clear outline in mechanical layer.

7. Check the layers in “Plot” column under “Layers To Plot” section for creating gerber files according to fabrication company instructions.
- Check following layers: GTO, GTP, GTS, GTL, GBL , GBS , GBP , GBO , GKO ,GPT , GPB , GM(Number)
- There will be no middle layer if you PCB board includes only 2-layers. All our design files include 2 layers which means you need to uncheck all middle layers (G1,G2,G3....)
- You can use the “Plot Layer” option and select the “Used On” to automatically check the used layers in your design.
8. Select “All Off” in “Mirror Layers” or uncheck every layer in “Mirror Layers” column
9. Uncheck all the layers in the plot column of “Mechanical Layers to Add to All Gerber Plots”
10. Check “Embedded apertures (RS274X)” under “Aperture” setting
11. Click on the “OK” button to generate gerber files.
12. Gerber files are automatically loaded in the Altium cam viewer. You can use “CAMtastic” view to verify that all layers have been generated correctly.
13. The gerber files should now be generated and saved in directory of your project.
14. You can also export gerber files to a new directory using following steps:
- Select File > Export > Gerber…
- Click on “OK”
- Select the path to the directory that you would like to save all the gerber files. (“gerbers” directory as example)
- Click on “OK” to export all the gerber files
15. Next, Generate the Drilling layer in Excellon format
16. Select File > Fabrication Outputs > NC Drill Files
17. Set the units in “inches” precision to “2:5” in NC Drill Setup window
18. Click on the “OK” button to generate drill files
19. The drill file should now be generated and saved as .TXT file in directory of your project.
20. You can also export file to a new directory using following steps:
- Select File > Export > Save Drill…
- Click on “OK”
- Select the path to the directory that you would like to save the drill file. (“gerbers” directory as example)
- Click on “OK” to export the drill file
21. Select the “Projects” view and highlight the “CAMtastic” cam file
22. Click on “Save As” under “File” and save the “CAMtastic” cam file.
23. Click on “Save”.
24. Select all the gerber/drill files in the directory that saved them and generate a compressed file in Zip format.

25. You can now submit the compressed Zip file that includes the gerber files to the PCB fabrication company of your choice.

## Kicad

1. Open the board file of your design file using Kicad. [4]
2. Select File > Plot
3. Check the layers in “Plot” window for creating gerber files according to fabrication company instructions.
- Check following layers: Top Copper (F.Cu), Soldermask (F.Mask), Silkscreen (F.SilkS), Bottom Copper (B.Cu), Soldermask (B.Mask), Silkscreen (B.SilkS), Board outline (Edge.Cuts)
4. Set the “Output directory” to save the generated gerber files. You can also use “Browse…” button to set the path to the directory.
5. Uncheck “Plot sheet reference on all layers” option.
6. Uncheck “Plot footprint values” option.
7. Check “Exclude PCB edge layer from other layers” option.
8. Check “Use Protel filename extensions” option.
9. Click on “Plot” button to generate and save gerber files in the specified output directory to save gerber files.
10. Next, configure the settings to generate drill file
11. Click on “Generate Drill File” button.
12. Set the “Output directory” to save the generated drill file. You can also use “Browse…” button to set the path to the directory. Use the same output directory as you selected to save the gerber files.
13. Check “Inches” as drill units.
14. Check “Decimal Format” as zeros format.
15. Check “PostScript” as drill map file format.
16. Check the “Merge PTH and NPTH holes into one file” option
17. Click on “Drill File” or press “Enter” to generate the drill file.
18. Click on “Close” to close “Drill Files Generation” Window.
19. Click on “Close” again to close “Plot” Window.
20. Verify the generated gerber files using a gerber viewer tool to make sure that all layers have been generated correctly.
21. Select all the gerber/drill files in the directory that saved them and generate a compressed file in Zip format.
22. You can now submit the compressed Zip file that includes the gerber files to the PCB fabrication company of your choice.

## 4. How to check and confirm PCB gerber files?

It is recommended to double check or triple check the final generated gerber files of your design to make sure there are no issues with process of gerber files generation. The PCB fabrication companies mostly provide online gerber file viewer tools that you can use to confirm your design once you upload your gerber files compressed as a Zip file. However, you can use other gerber file viewer to check your design files before submitting the gerber files.

The following gerber viewer tools are recommended:

- Online Gerber Viewer (https://www.gerber-viewer.com/)
- gerbv (https://sourceforge.net/projects/gerbv/)

Select all the generated gerber file layers in the “gerbers” directory and view them to make sure all the layers are aligned.

## 5. Where to send PCB gerber files for fabrication?

The process to send the gerber files for fabrication may differ from company to company but there are general steps you can follow to send your gerber files for fabrication.

1. Select the fabrication company (Here are our recommended fabrication companies)
- Seeed Fusion PCB
- PCBWay
- OSH Park ~
- JLCPCB
2. Create an account on PCB fabrication website or use temporary login if it is available
3. Select the fabrication service
4. Upload the compressed Zip file that includes your gerber files
5. Select the available options based on your design requirements. The standard options for most of our projects:
- PCB Layers: 2 Layers
- PCB dimensions should update based on your uploaded gerber files, but you can manually entry the dimensions as well
- PCB quantity can vary based on your requirements (Minimum 5)
- PCB Color can be changed if the fabrication company offers the option. The defualt option has the fastest turnaround time.
- Surface Finish: HASL
- Copper Weight, Minimum Drill Hole Size, Trace Width , Minimum Solder Mask Dam doesn’t require to be changed and the default value works
6. Check the uploaded gerber files using online gerber viewer tool if it is offered by the fabrication company and make sure there are no issues.

7. Add the uploaded design to the order
8. Add another design if you are doing multiple orders
9. Proceed to the checkout and enter your billing and shipment information
10. Select the shipping method
11. Submit your order for production
12. The technician will contact you for additional information or corrected files if there are issues with your design files.
13. You will receive an email when your design goes to production
14. You will receive another email once your PCBs are produced and shipped

This includes the instructions for fabrication of PCB designs based on generated gerber files.

## Reference

1. https://learn.sparkfun.com/tutorials/pcb-basics/all
2. https://www.hi5electronics.co.uk/what-is-pcb-fabrication/
3. https://support.jlcpcb.com/article/42-how-to-export-altium-pcb-to-gerber-files
4. https://support.jlcpcb.com/article/44-how-to-export-kicad-pcb-to-gerber-files

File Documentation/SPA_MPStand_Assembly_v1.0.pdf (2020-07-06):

# Sip & Puff Mouthpiece Stand

# ASSEMBLY MANUAL

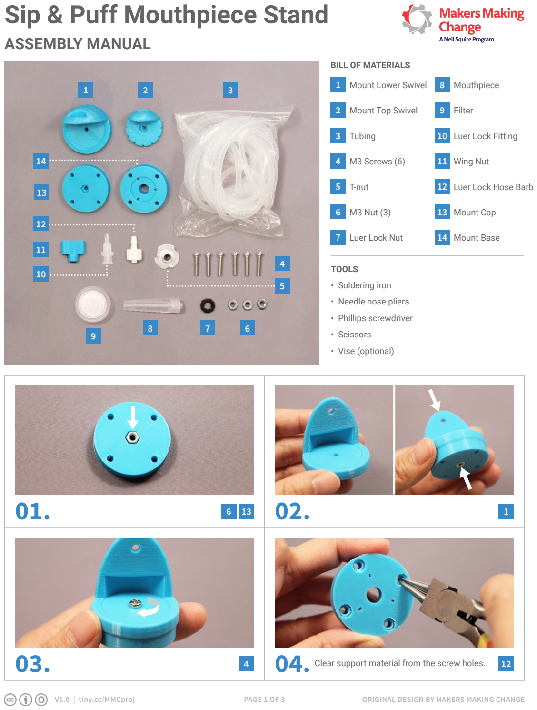
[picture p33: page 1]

PAGE 1 OF 3

04.

BILL OF MATERIALS

- Soldering iron
- Needle nose pliers
- Phillips screwdriver
- Scissors
- Vise (optional)

TOOLS

1 | 2 | 3

4

5

8 | 7 | 6
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
### 5 T-nut

### 4 M3 Screws (6)

### 3 Tubing

### 2 Mount Top Swivel

### 1 Mount Lower Swivel

### 6 M3 Nut (3)

### 9 Filter

### 7 Luer Lock Nut

### 10 Luer Lock Fitting

### 8 Mouthpiece

### 11 Wing Nut

Clear support material from the screw holes. 12

13 1

### 13 Mount Cap

### 14 Mount Base

### 12 Luer Lock Hose Barb

01. 02.

03.

V1.0 | tiny.cc/MMCproj | ORIGINAL DESIGN BY MAKERS MAKING CHANGE

# Sip & Puff Mouthpiece Stand

# ASSEMBLY MANUAL

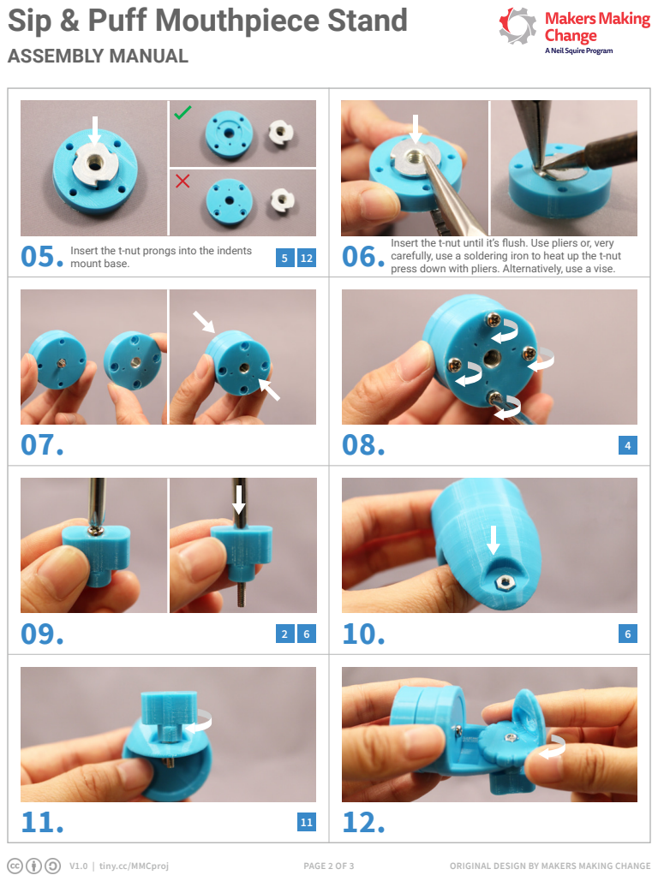
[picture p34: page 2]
PAGE 2 OF 3; mount base.

Insert the t-nut until it’s flush. Use pliers or, very
carefully, use a soldering iron to heat up the t-nut
press down with pliers. Alternatively, use a vise.

Insert the t-nut prongs into the indents

# Sip & Puff Mouthpiece Stand

# ASSEMBLY MANUAL

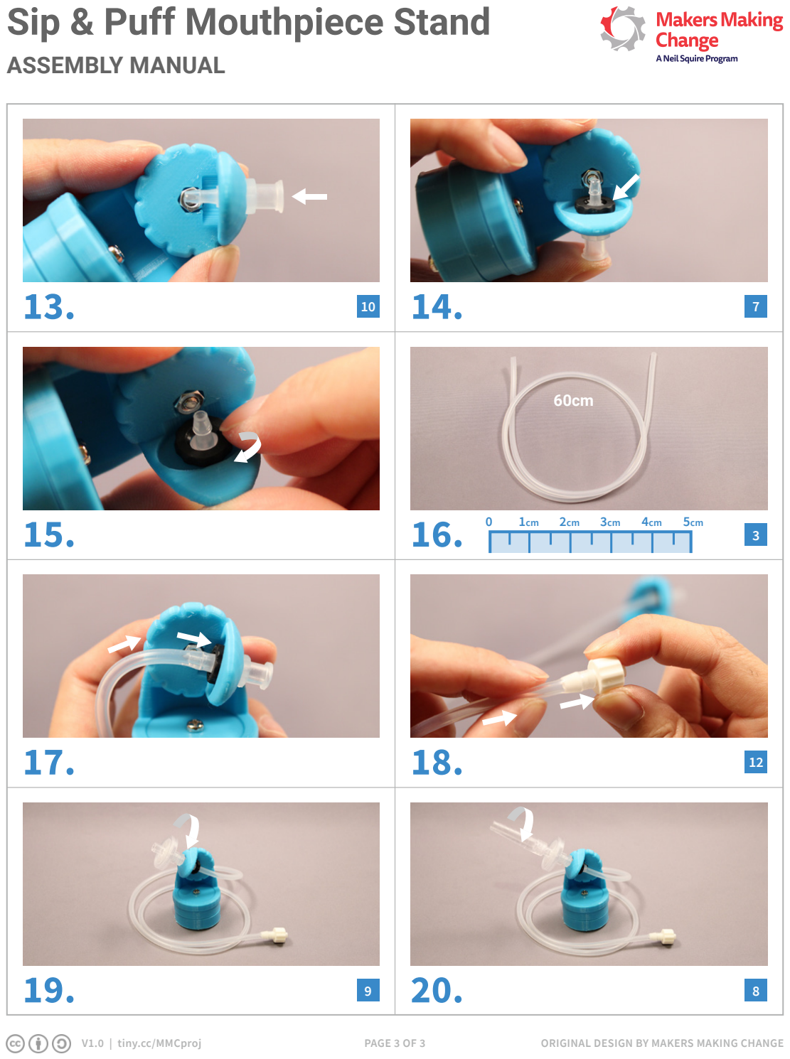
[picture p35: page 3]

19. 20.
17. 18.
15. 16.
13. 14.

PAGE 3 OF 3

Prepare 60cm
of tubing.
0 | 1cm | 2cm | 3cm | 4cm | 5cm

10 7

3

3

3

12

9 8

60cm

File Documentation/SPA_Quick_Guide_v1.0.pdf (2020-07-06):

Analog Sip and Puff: One Page Quick Setup Guide

Notes:
For overview, detailed instructions, cleaning, battery and specs, refer to document: Analog Sip and Puff User Guide
1) Hook up the air tube:
Connect the mouthpiece to the Sip and Puff Switch main box, as shown in Fig1:

Fig. 1

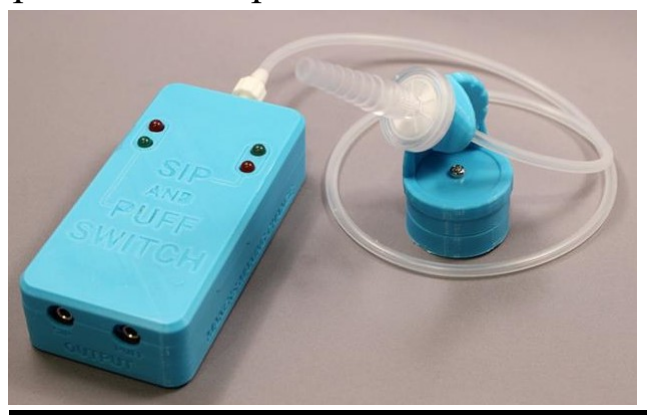
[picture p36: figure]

2) Turn on the main box:
Slide the power switch left, (center of fig 2) towards the air tube connection, using a pen tip.

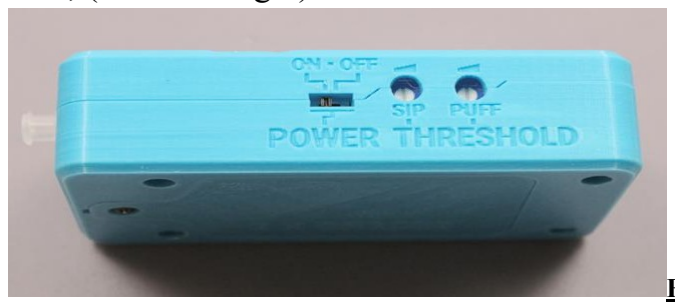
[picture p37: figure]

Fig. 2

3) Reset The Sip and Puff thresholds:
Using a small flat screwdriver, turn both thresholds (Fig2, right of switch) fully clockwise.
4) Set The Sip threshold:
Dial the first adjustment left, until the red (sip) LED just goes out (and stays out).
5) Set The Puff threshold:
Dial Second adjustment left, until the red (puff) LED just goes out (and stays out).
6) Test the unit:
(Disinfect mouthpiece!) Sip and puff on the mouthpiece to confirm proper operation. The red Puff LED (Left Fig.1) should turn on when you puff on the mouthpiece. The red Sip LED (Right Fig.1) should turn on when you sip on the mouthpiece.
7) Attach your controlled devices to Sip & Puff switch:
Hook your puff device to 3mm Jack (Fig1, case bottom left) on the main unit. Hook your sip device to 3mm Jack (Fig1, case bottom right) on the main unit.

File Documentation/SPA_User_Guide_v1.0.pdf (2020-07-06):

Analog Sip and Puff User Guide

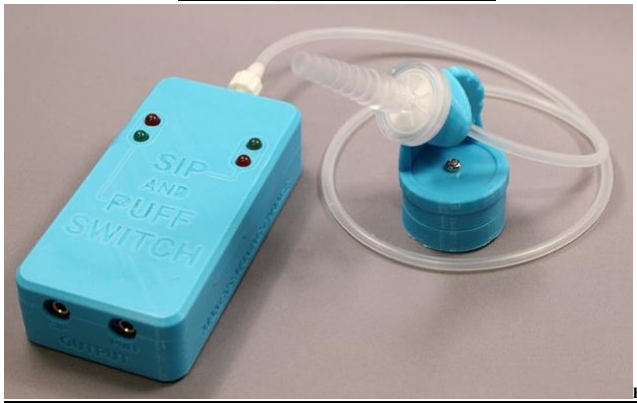
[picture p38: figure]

Fig. 1

Overview:

The MMC Analog Sip and Puff Switch is an assistive switch able to be operated by softly sipping or puffing air in or out of a mouthpiece. The user should have the ability to blow air into, or draw or draw air from a straw . The switch is not recommended for persons who are unable to consciously control air movement in their lungs or mouth. The Analog Sip and Puff Switch consists of a rectangular control box to which an air tube and mouthpiece can be attached. Inside the box there is an air pressure sensor, and two independent momentary switches. The first switch normally triggers when drawing in (sipping) air through the mouthpiece. The second switch normally triggers when blowing (puffing) air through the mouthpiece. The sensitivity level of the sip and puff functions are individually adjustable using two side mounted controls that can be set with a small screwdriver. The internal switches on the unit connect to the external being controlled via two 3mm audio jacks using standard 3mm mono audio cables.

Setup & Adjustment:

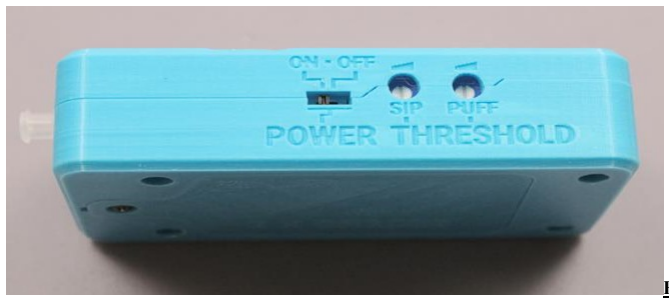
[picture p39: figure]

Fig. 2

To get started, connect the mouthpiece to the Sip and Puff Switch main box as shown in Fig 1. The unit should be turned on by sliding the power switch (Fig. 2) left, towards the air tube connection, using a pen tip. The switch is recessed to reduce the chance of the unit being turned on or off accidentally. Once the unit is turned on, you should notice some LED’s glowing on the top panel. Normally, you should not see a red LED turned on, unless the user is sipping or puffing into the mouthpiece, as red indicates a triggered (on) state. The quickest way to adjust thresholds, is to use a small screwdriver and dial both adjustments fully clockwise (maximum sensitivity). Then, dial the left (sip) adjustment counterclockwise, until the red sip LED goes out, and the green sip LED (closest to air tube inlet) just stays on. Next, dial the right (sip) adjustment counterclockwise, until the red puff LED goes out, and the green puff LED (furthest from air tube inlet) just stays on. If the sip or puff sensitivity triggers too easily, it’s sensitivity can be reduced by further turning the adjustment counterclockwise.

Installing or changing batteries:

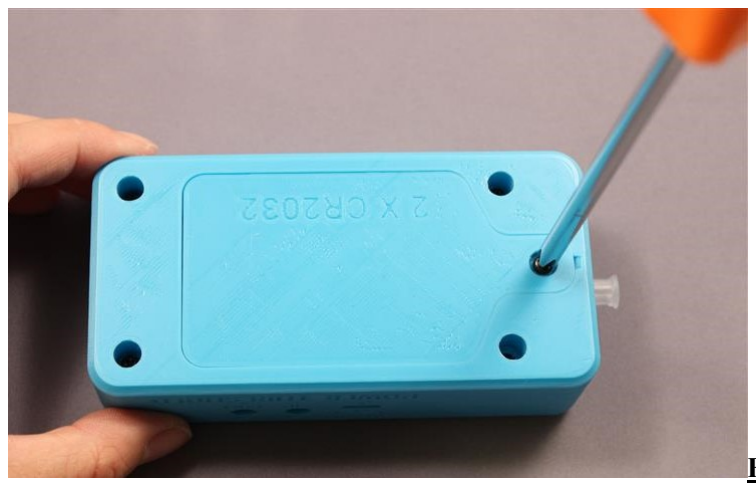
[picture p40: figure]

Fig. 3

The batteries in the Sip and Puff Switch can be changed by using a medium sized Phillips screwdriver, to remove the battery lid screw (closest screw to air tube connector) as shown above.

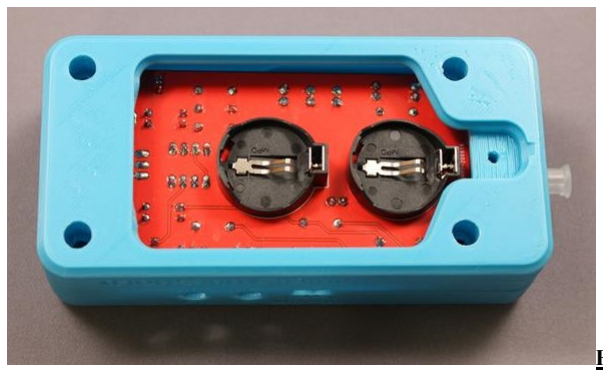
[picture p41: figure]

Fig. 4
The Sip and puff switch accepts two CR2032 coin cells into the round battery holders shown in Fig.4. The battery positive terminal is marked with a ‘+’ which must face up while being installed
Important: The lithium batteries should be changed in pairs to prevent damage to the batteries.

Specifications:

Size: 119mm X 56mm X (the unit sits 11mm higher with the mounting adaptor attached.) Switch connectors: Dual 3mm mono audio type jacks. Accepts standard 3mm mono plug cables. Recommended tubing 4mm OD 2mm ID Food
Maximum switching voltage: 48V, DC or AC.
Maximum switching current: 1 Amp, DC or AC.
Battery: Two CR2032 3V cell (replaceable)
Current draw 6.5ma
Expected battery life: 24 hours.
Cleaning: Clean or disinfect with bleach 2 teaspoons of 5 percent laundry bleach in one cup of water. Do not use alcohol on the air tube or air tube fitting.

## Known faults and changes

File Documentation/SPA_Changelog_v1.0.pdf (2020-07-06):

V1.0 | JUNE 2020

# Sip and Puff Switch

# CHANGELOG

© 2020 by Neil Squire. (https://neilsquire.ca/) “Sip and Puff Switch Changelog” is licensed under the CC BY SA 4.0 License: http://creativecommons.org/licenses/by-sa/4.0
Design files available at https://www.makersmakingchange.com/project/sip-and-puff-switch/ | PAGE 1 OF 2

V1.0

# - Initial Release

V1.0 | JUNE 2020

# Sip and Puff Switch

# CHANGELOG

© 2020 by Neil Squire. (https://neilsquire.ca/) “Sip and Puff Switch Changelog” is licensed under the CC BY SA 4.0 License: http://creativecommons.org/licenses/by-sa/4.0
Design files available at https://www.makersmakingchange.com/project/sip-and-puff-switch/ | PAGE 2 OF 2

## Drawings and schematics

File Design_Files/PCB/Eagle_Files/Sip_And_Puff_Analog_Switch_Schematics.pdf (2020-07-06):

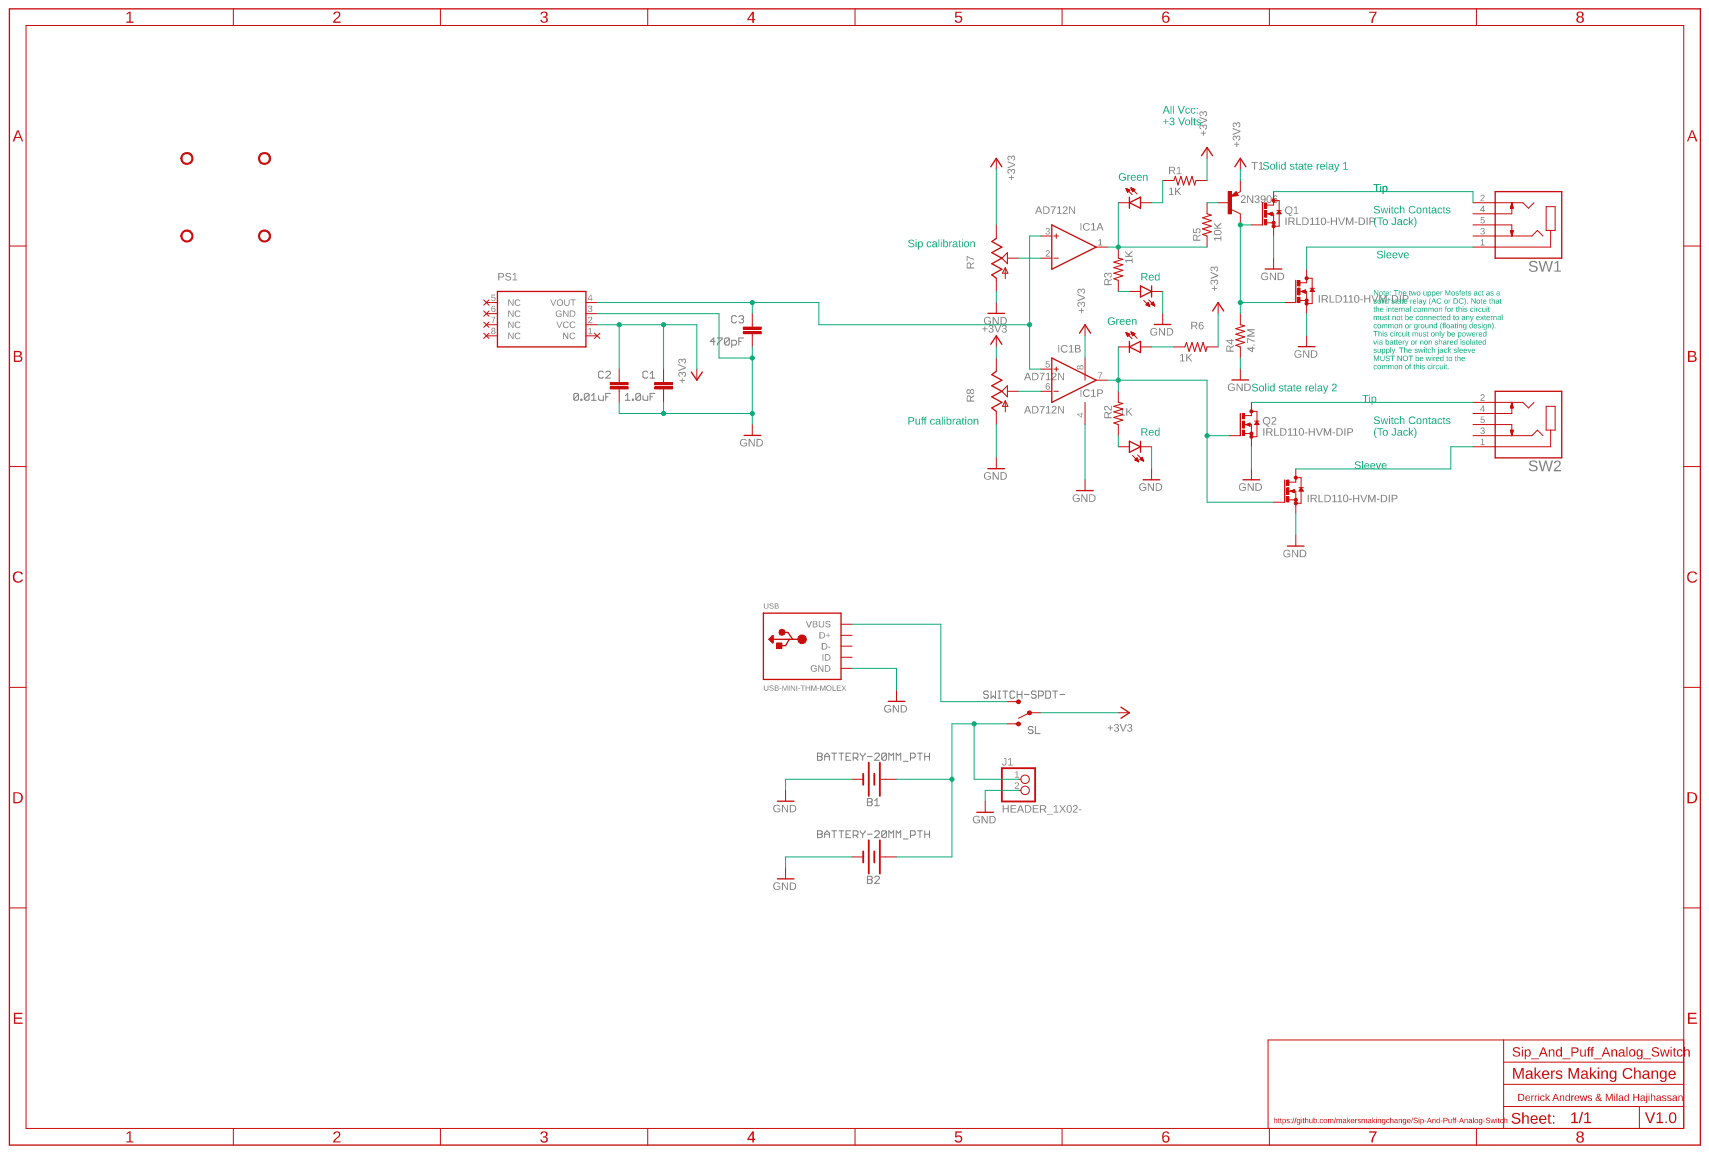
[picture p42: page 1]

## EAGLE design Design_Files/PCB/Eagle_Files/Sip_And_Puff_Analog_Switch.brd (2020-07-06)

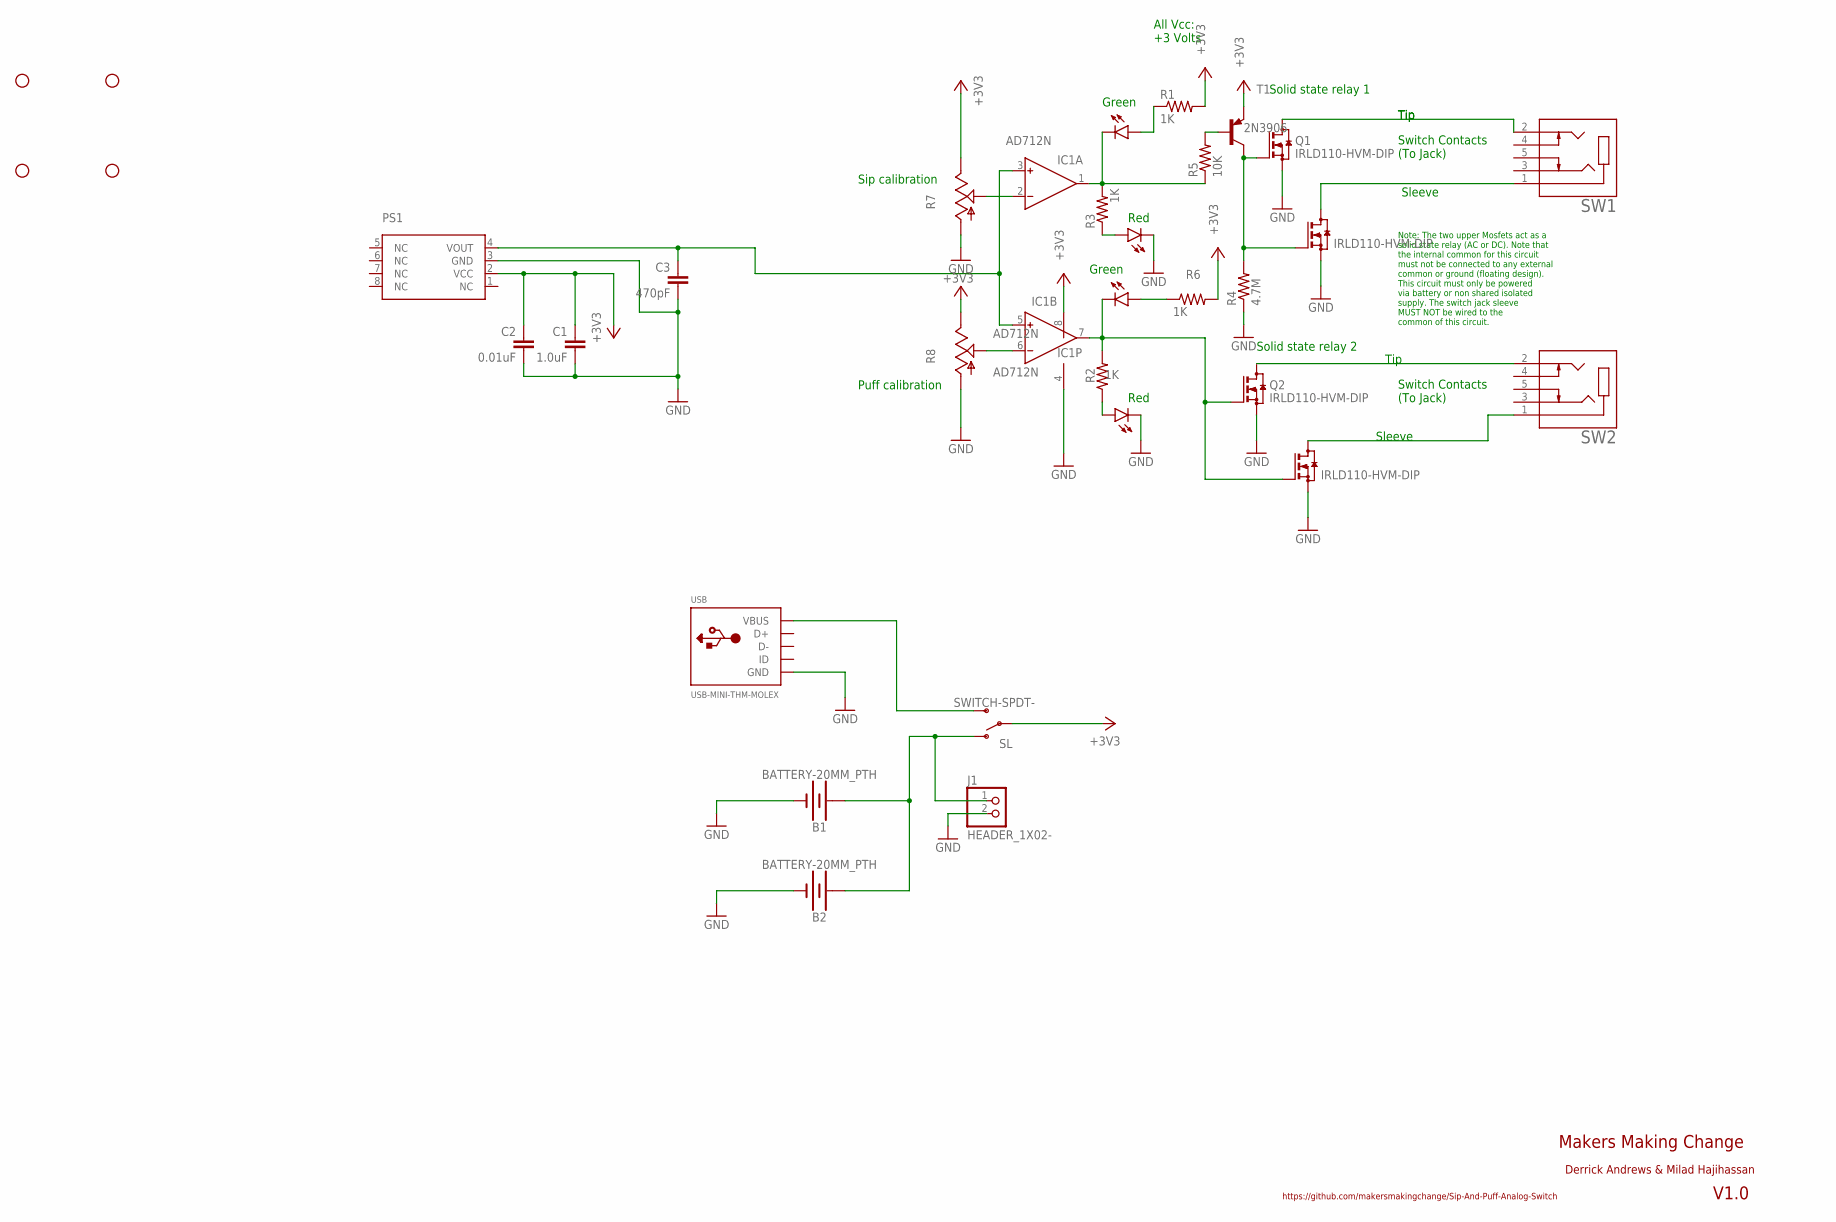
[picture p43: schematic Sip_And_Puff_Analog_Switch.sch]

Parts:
B1, B2: BATTERY-20MM_PTH; BATTCOM_20MM_PTH
C1: 1.0uF; CAP-PTH-SMALL-KIT
C2: 0.01uF; CAP-PTH-SMALL-KIT
C3: 470pF; CAP-PTH-SMALL-KIT
IC1: AD712N; DIL08
J1: HEADER_1X02-; 1X02
LED1, LED2: LED5MM-RED; LED_5MM_RED
LED3, LED4: LED5MM-GREEN; LED_5MM_GREEN
PS1: MPX-; MXP_SOP8
Q1, Q2, Q3, Q4: IRLD110-HVM-DIP; HVM-DIP
R1, R2, R3, R6: 1K; RESISTOR_0207/7
R4: 4.7M; RESISTOR_0207/7
R5: 10K; RESISTOR_0207/7
R7, R8: TRIM-3386C; 3386C
SL: SWITCH-SPDT-; SPDT-RA
STANDOFF1, STANDOFF2, STANDOFF3, STANDOFF4: STAND-OFF-; STAND-OFF
SW1, SW2: CUI_SJ1-3535NGSJ1-3535NG; CUI_SJ1-3535NG
T1: 2N3906; TO92-EBC
USB: USB-MINI-THM-MOLEX; USB-MINIB-THM-MOLEX

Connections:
+3V3: C1.1, C2.1, IC1.8 (V+), PS1.2 (VCC), R1.2, R6.2, R7.E, R8.E, SL.2, T1.E
GND: B1.-, B2.-, C1.2, C2.2, C3.2, IC1.4 (V-), J1.2, LED1.K (C), LED2.K (C), PS1.3 (GND), Q1.2 (S), Q2.2 (S), Q3.2 (S), Q4.2 (S), R4.1, R7.A, R8.A, USB.GND
unnamed: IC1.7 (OUT), LED4.K (C), Q2.1 (G), Q4.1 (G), R2.2
unnamed: SL.3 (S), USB.VBUS
unnamed: LED4.A, R6.1
unnamed: B1.+, B2.+, J1.1, SL.1 (O)
unnamed: Q3.3 (D), SW1.1
unnamed: Q1.3 (D), SW1.2
unnamed: Q1.1 (G), Q3.1 (G), R4.2, T1.C
unnamed: R5.2, T1.B
unnamed: IC1.1 (OUT), LED3.K (C), R3.2, R5.1
unnamed: IC1.2 (IN-), R7.S
unnamed: IC1.6 (IN-), R8.S
unnamed: C3.1, IC1.3 (IN+), IC1.5 (IN+), PS1.4 (VOUT)
unnamed: Q2.3 (D), SW2.2
unnamed: Q4.3 (D), SW2.1
unnamed: LED3.A, R1.1
unnamed: LED2.A, R2.1
unnamed: LED1.A, R3.1

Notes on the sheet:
Makers Making Change
V1.0
https://github.com/makersmakingchange/Sip-And-Puff-Analog-Switch
Derrick Andrews & Milad Hajihassan
All Vcc: +3 Volts
Switch Contacts (To Jack)
Note: The two upper Mosfets act as a solid state relay (AC or DC). Note that the internal common for this circuit must not be connected to any external common or ground (floating design). This circuit must only be powered via battery or non shared isolated supply. The switch jack sleeve MUST NOT be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
Tip
Sleeve
Solid state relay 1
Solid state relay 2
Sip calibration
Puff calibration
Green
Red

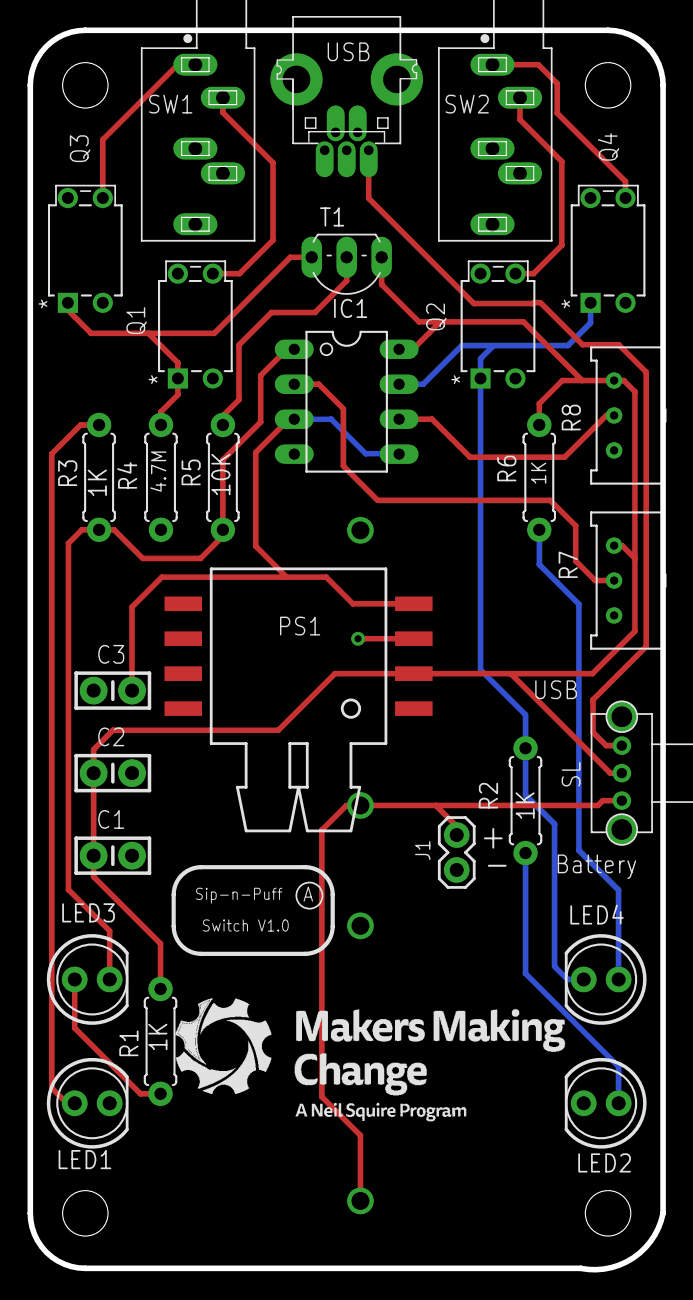
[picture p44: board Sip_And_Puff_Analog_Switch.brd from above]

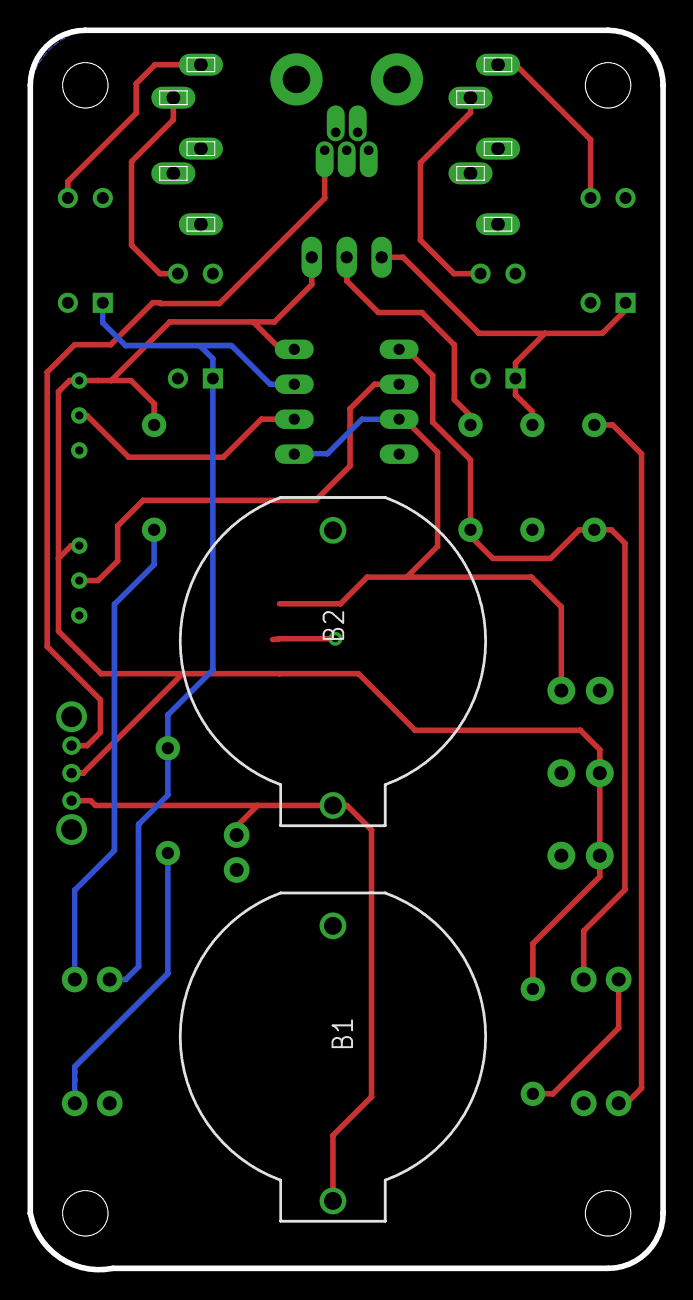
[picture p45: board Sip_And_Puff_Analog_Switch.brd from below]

Board: 2 copper layers, 46.0 x 90.1 mm, 33 parts (2 on the bottom side), 19 nets.

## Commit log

2020-07-02 Pre-publish commit
    [M3WingNut2.scad, MouthP_MntBase.scad, MouthP_MntCap.scad, MouthP_MntLswivel.scad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]
2020-07-02 Rename instructions to assembly for clarity
2020-07-06 Update BOM
    [SPA_BOM_v1.0.xlsx]
2020-07-07 Update SPA_BOM_v1.0.xlsx
    Correct M3 screw length
    [SPA_BOM_v1.0.xlsx]
2020-07-08 Convert to stl binary
    Binary version of stl rather than text version provides a download link and reduces confusion.
    [SPA_MP_Base.stl, SPA_MP_M3WingNut.stl]
2020-07-10 Update SPA_BOM_v1.0.xlsx
    Add missing two position header.
    [SPA_BOM_v1.0.xlsx]
2020-10-13 Update SPA_MP_Lower_Swivel.stl
    Replace text-based stl wth binary version for consistency.
    [SPA_MP_Lower_Swivel.stl]
2020-10-13 Add 3mf files
    [SPA_All-PETG.3mf, SPA_All-PLA.3mf, SPA_Encl_Set_PLA.3mf]

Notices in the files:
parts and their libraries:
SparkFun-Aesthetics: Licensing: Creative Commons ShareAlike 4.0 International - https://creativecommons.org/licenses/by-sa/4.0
